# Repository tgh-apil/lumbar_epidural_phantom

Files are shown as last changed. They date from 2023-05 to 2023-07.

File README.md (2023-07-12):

# APIL Normal Spine Epidural Phantom
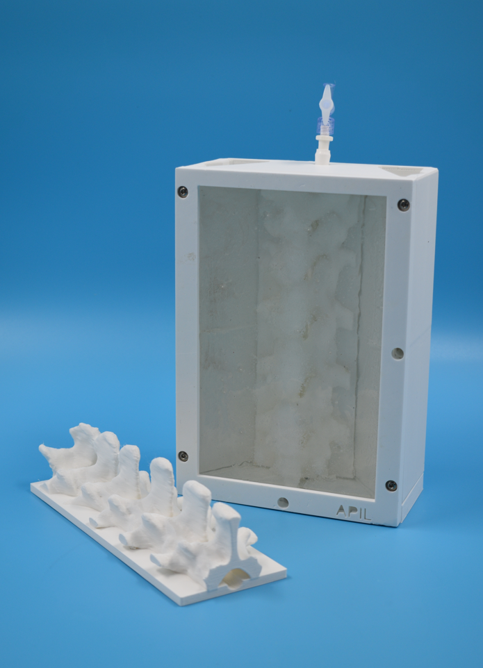
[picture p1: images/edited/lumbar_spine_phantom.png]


3D Printed lumbar epidural spine based on CT data.  Our epidural spine phantom is encased in an synthetic, shelf-stable gel which has a realistic tactile feel to human muscle and is echogenic.  We can augment the echogenic properties to be transparent (clear gel) to mimicing that of biological tissue (opaque) based on the learning objective. Additionally, the Normal Spine Epidural Phantom contains an echogenic faux-thecal sac to replicate loss-of resistance on puncture.  The faux-thecal sca can be inflated with water to simulate spinal fluid.

This phantom is designed with the ability to adjust the depth of 'tissue' over the spine to simulate different anatomies/difficulties.  By default, the most surface spinous process is embedded underneath approximately +5 mm of echogenic gel.  However, we have also produced this phantom with deeper embeds -- the two most common being +10 mm and +17 mm.  These different depths require different case lids which are provided in this repo.  Please refer to the table provided in the **3D Printing Components** section of this guide to reference which lid will fit the depth.

This model was developed at the [Lynn & Arnold Irwin Advanced Perioperative Imaging Lab](https://apil.ca), Toronto General Hospital, University Health Network.

# Purchasing Information
To purchase this phantom, please email <apil@uhn.ca> and a represtative will be in touch with you with more details.

**A purchased phantom contains the following**:

1. Fully assembled Normal Spine Phantom 
   1. Spine embed depth can be customized to order.
2. Custom table clamp to hold phantom to tabe surface

# Ultrasound Images
Coming soon

# Care and Maintenance
1. Apply generous amount of ultrasound gel to surface of phantom.
2. Inflate thecal sac with water and ensure quickturn locks are closed

# Materials & Equipment

## Hardware

- 2 x M5*14 pins
- 6 x M4*25 Bolts
- 4 x M4*8 Bolts (for use with default lid)
- 4 x M4*14 Bolts (for use with 5mm lid)
- 4 x M4*16 Bolts
- 4 x M4*20 Bolts (for use with 12mm lid)
- 4 x M4*20 Bolts (for use with case bottom)
- 2 * Quick-turn Lock
- 8 mm ID Silicone Tubing (as low durometer as possible)
- 2 * Tube Fittings

## Printing Equipment

- Polylactic Acid (PLA)
- Bridge Nylon
- Fused Deposition Modelling 3D printer

## Casting Equipment

- Ballistics Gel
  - Gelatin #3 from [Humimic Medical](https://humimic.com/product/gelatin-3-medical-gel-by-the-pound/)
- Graphite Powder (optional)
  - used to replicate echogenic scatter of muscle
- Slowcooker
- Two-part Platinum Cure Silicone Rubber (or equivalent)
  - Available from [Smooth-On](https://www.smooth-on.com/products/dragon-skin-30/)
- Degas Chamber (Optional)

# Assembly Instructions

## Printing

This repo includes **stl** files for each printed part.

In general, we use the following settings for *all* parts of this phantom:

<table>
    <tr>
        <td><b>Material</b></td>
        <td><b>Colour</b></td>
        <td><b>Nozzle Temp (C)</b></td>
        <td><b>Bed Temp (C)</b></td>
        <td><b>Infill (%)</b></td>
        <td><b>Perimiters (#)</b></td>
    </tr>
    <tr>
        <td>PLA</td>
        <td>White</td>
        <td>210.0</td>
        <td>60.0</td>
        <td>10.0</td>
        <td>2</td>
    </tr>
    <tr>
        <td>Bridge Nylon</td>
        <td>Natural</td>
        <td>250.0</td>
        <td>80.0</td>
        <td>15.0</td>
        <td>3</td>
    </tr>
</table>

## Silicone Casting

### Silicone Mold Casting

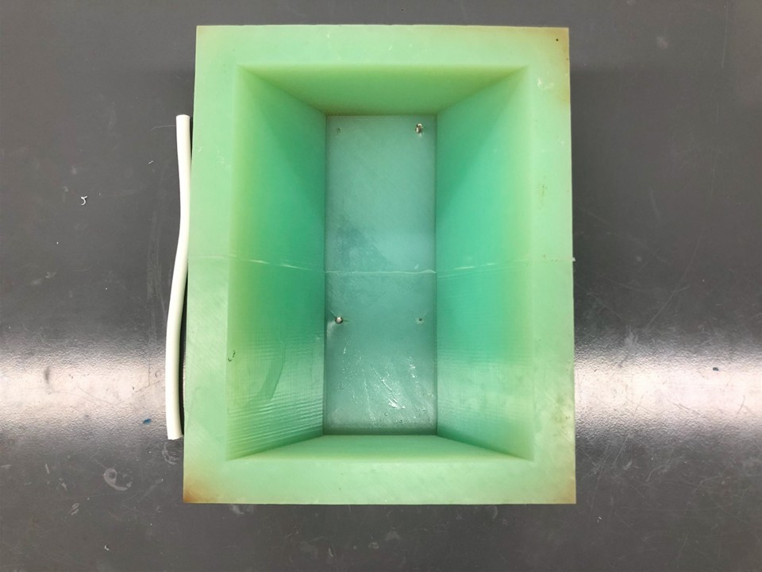
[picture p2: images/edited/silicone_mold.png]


1. Print all components in the directory */molds/* using the PLA printing settings outlined above.
2. Assemble mold parts 1 and 2 and together using:
   1. 2 x M5*14 pins
   2. 6 x M4*25 bolts
3. Mix **2700 g** of silicone according to manufacturers instructions.
    - Degassing the silicone is encoraged, but optional.
    - Adding colourant to silicone is optional.
4. Pour all silicone into the assembled mold.
5. Allow silicone to cure according to manufacturer's instructions.
6. Carefully disassmble the mold and release the silicone.
   - **NOTE:** This step can be very difficult.  Procede with caution and patience to avoid damaging the silicone shell.

## 3D Printing Components

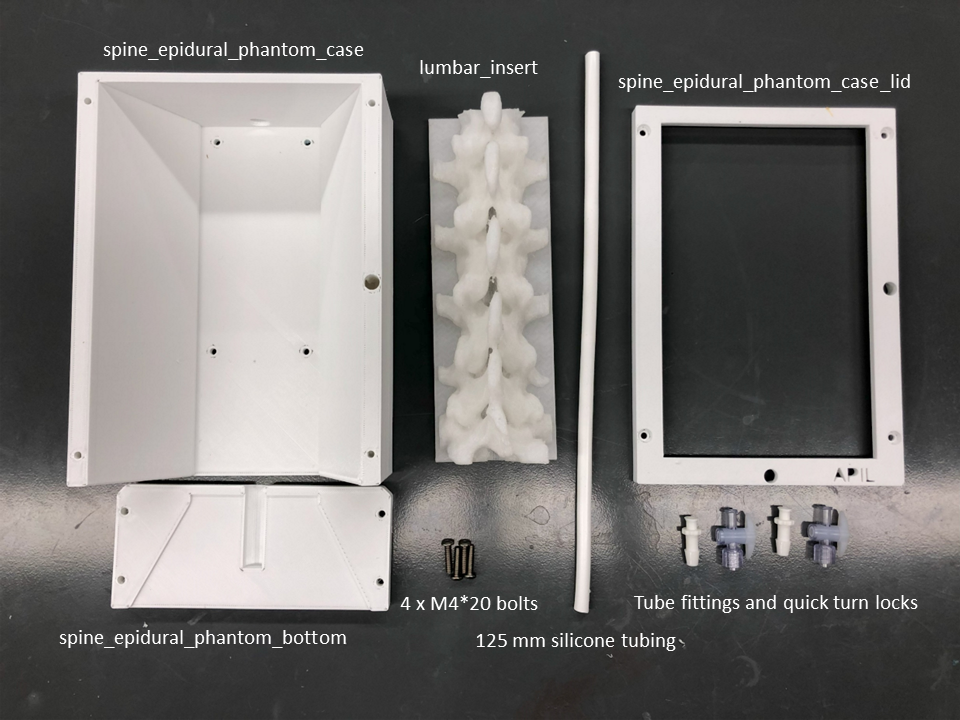
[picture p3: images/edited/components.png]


1. Print all components in the directory */insert/* using the Bridge printing settings outlined above.
   1. Refer to the following table for the appropriate lid to print depending on depth of spine embed:

<table>
    <tr>
        <td><b>Spine Embed Depth</b></td>
        <td><b>Corresponding Lid Type</b></td>
    </tr>
    <tr>
        <td>5 mm</td>
        <td>spine_epidural_phantom_case_default_lid</td>
    </tr>
    <tr>
        <td>10 mm</td>
        <td>spine_epidural_phantom_case_5mm_lid</td>
    </tr>
    <tr>
        <td>17 mm</td>
        <td>spine_epidural_phantom_case_12mm_lid</td>
    </tr>
</table>

2. Print all components in the directory */case/* using the PLA printing settings outlined above.
3. Carefully remove **all** supports from the part when complete.

## Ballistics Gel Casting

1. **CAUTION:** Use appropriate heat-proof gloves when working with liquefied ballistic gel and/or heat gun.
2. **CAUTION:** work **only** in a very well ventilated area.  A fumehood is *highly* recommended.

### Ballistics Gel Casting

1. Melt at least **1500 g** gel in crockpot @ 105C - 115C (approx. 225F - 240F).
2. If the gel does not contain graphite powder, slowly add graphite powder into fully liquefied mixture until saturated.
   1. For this phantom, this step is optional.  You can leave it clear if the learning objective is to insert an epidural without the use of ultrasound.
3. Thread a length of silicone tubing through the scoliotic sipne to replicate the thecal sac.  The length should be just enough to reach end-to-end of the scoliotic spine.
4. Anchor spine insert and thecal sac silicone tube into the silicone mold with 4 x M4*16 bolts.
5. Pour gel into mold until you reach the required depth of submersion.
6. Allow gel to fully cool before removal from silicone molds.
7. Remove previously installed silicone tube.
8. Install a new silicone tube measuring 125 mm.
   1. we use a longer silicone tube in this step so the ends of the tubing extend well past the case for ease of access.

## Phantom Assembly

1. Insert spine with gel block into printed case.
2. Thread both ends of silicone tubing through printed case.
3. Attach case bottom with 4 x M4*20 bolts.
4. Attach case lid with appropriate M4 bolts.
5. Attach a tube fitting to each end of the silicone tube.
6. Attach a quick-turn lock to each end of the tube fittings.

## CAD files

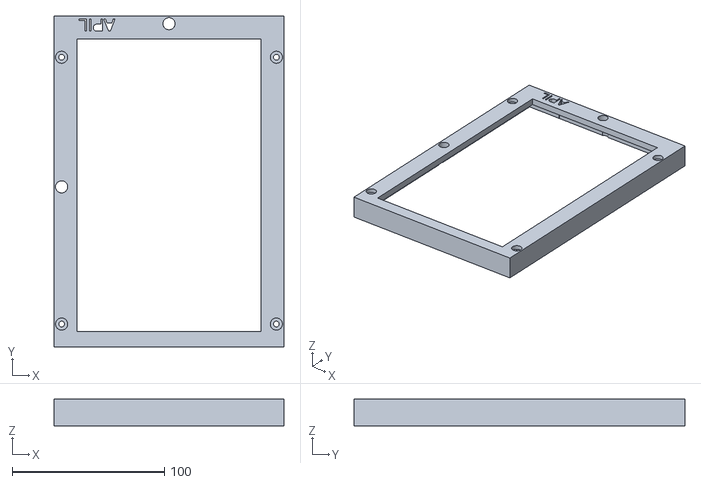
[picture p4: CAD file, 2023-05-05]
case/spine_epidural_phantom_12mm.stl
150.9 x 217.0 x 17.5

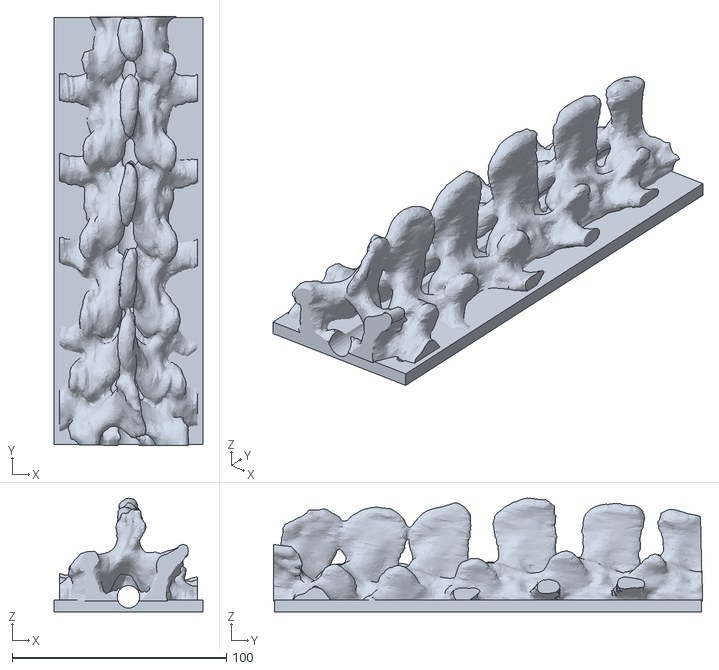
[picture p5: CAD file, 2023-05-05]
insert/lumbar_insert.stl
69.6 x 200.5 x 53.1

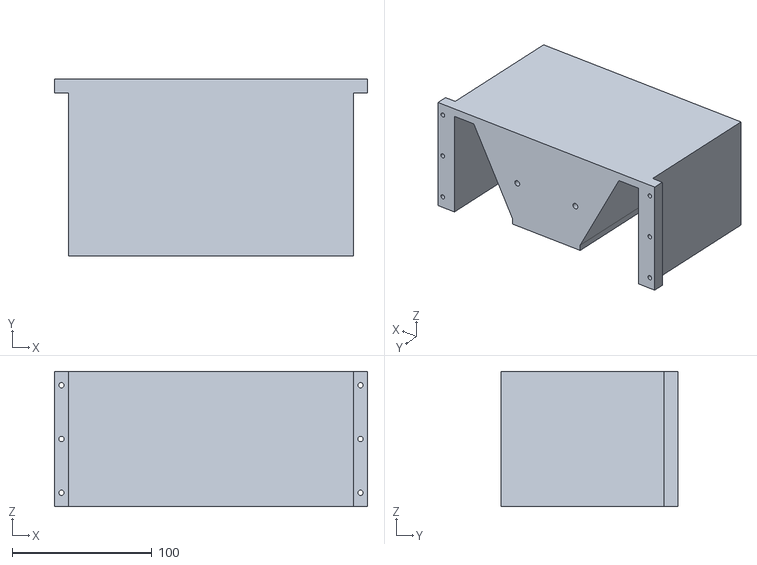
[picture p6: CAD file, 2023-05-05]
molds/spine_epidural_phantom_mold_1.stl
224.1 x 127.0 x 97.0

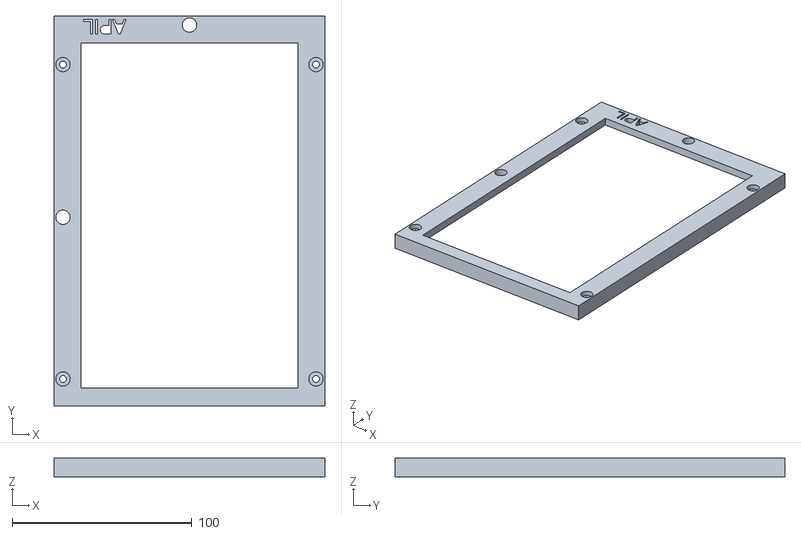
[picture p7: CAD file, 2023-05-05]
case/spine_epidural_phantom_5mm.stl
150.9 x 217.0 x 10.5

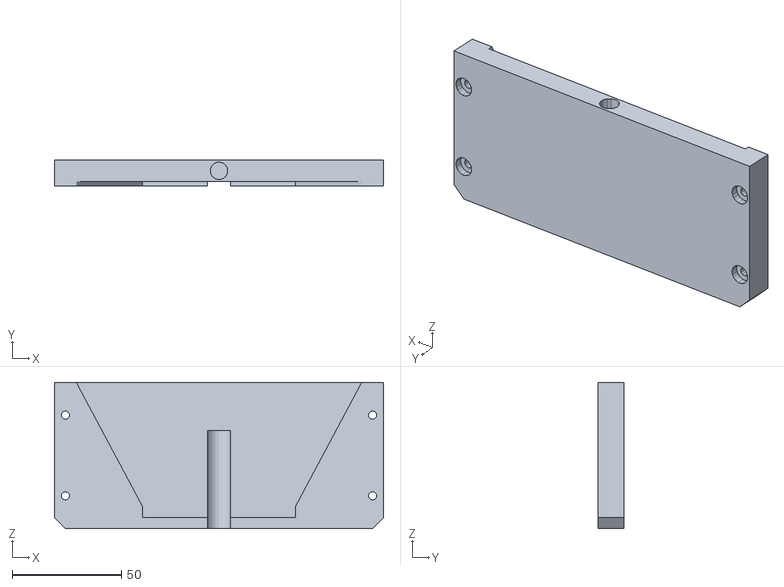
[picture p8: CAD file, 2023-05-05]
case/spine_epidural_phantom_case_bottom.stl
150.9 x 12.0 x 67.0

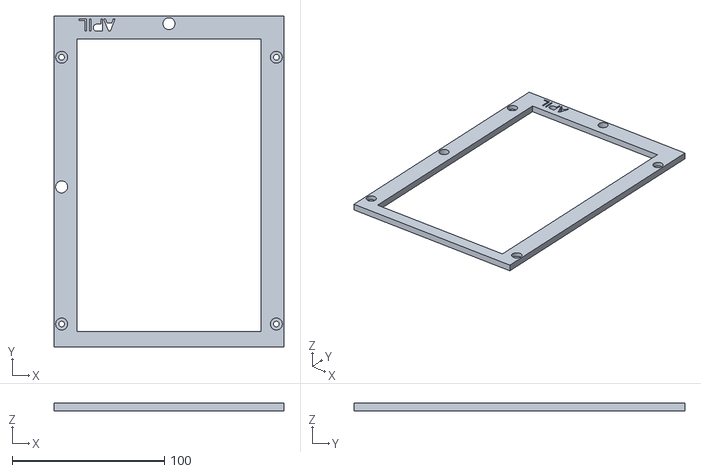
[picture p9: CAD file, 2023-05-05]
case/spine_epidural_phantom_case_default_lid.stl
150.9 x 217.0 x 5.00

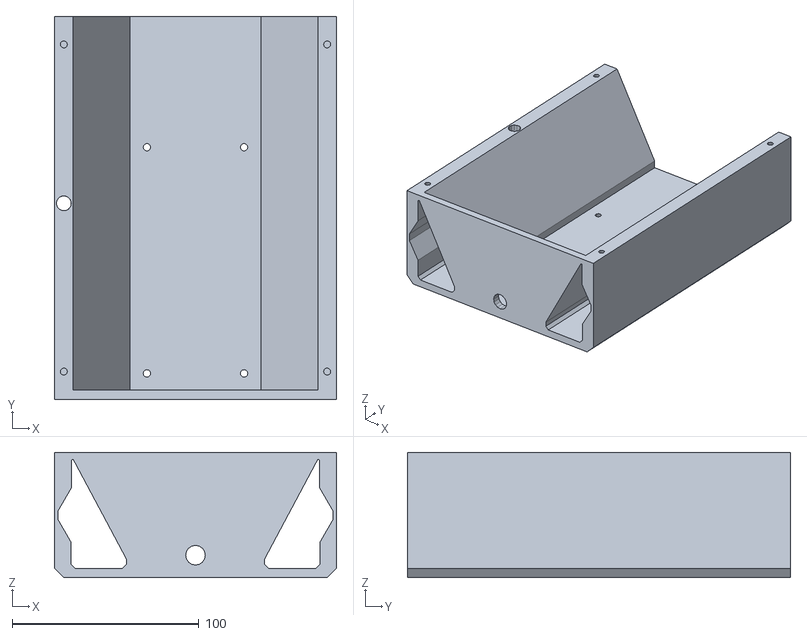
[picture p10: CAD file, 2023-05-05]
case/spine_epidural_phantom_case.stl
150.9 x 205.0 x 67.0

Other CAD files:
molds/spine_epidural_phantom_mold_2.stl

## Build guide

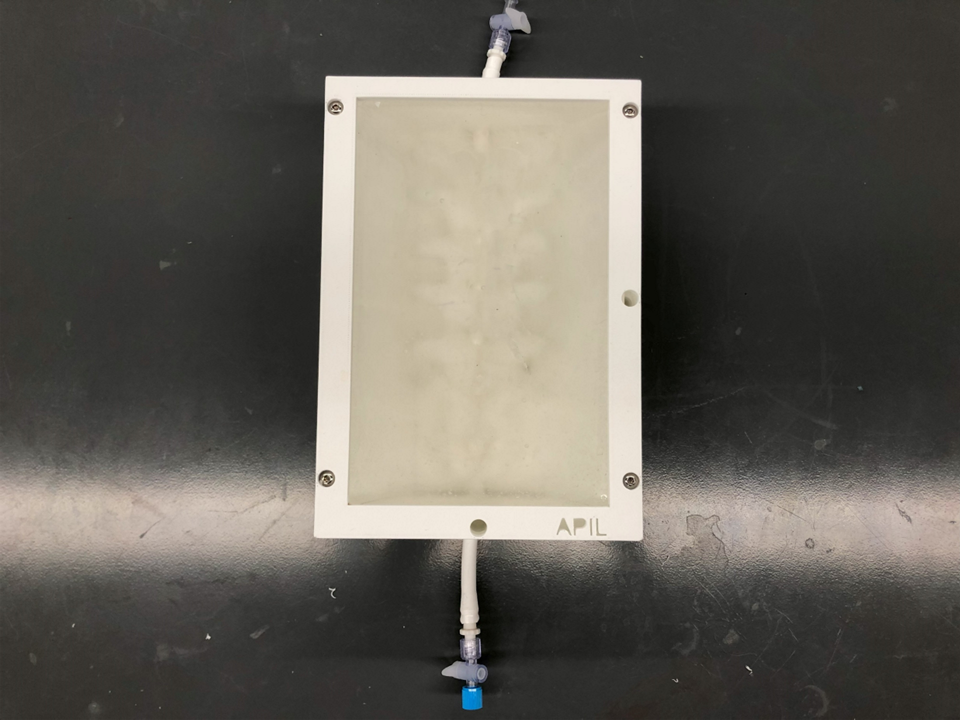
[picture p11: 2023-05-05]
images/edited/assembled.png
